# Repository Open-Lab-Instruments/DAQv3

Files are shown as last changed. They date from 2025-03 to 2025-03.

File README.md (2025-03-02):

# DAQv3
A Dual-Channel, Low Noise, Modular, 100 kHz Bandwidth, 24-Bit Data Acquisition (DAQ) Device / FFT Signal Analyzer

# Table of Contents

- **[Introduction](#introduction)**
- **[CAD Model](#cad-model)**
- **[Modules](#modules)**
  - [AnalogConversion_v1](#AnalogConversion_v1)
  - [AnalogConversion_v2](#AnalogConversion_v2)
  - [AnalogConversion_v3](#AnalogConversion_v3)
  - [Backplane_v1](#Backplane_v1)
  - [DigitalBackend_v1](#DigitalBackend_v1)
  - [PowerSupply_5V_v1](#PowerSupply_5V_v1)
  - [PowerSupply_5V_v2](#PowerSupply_5V_v2)
  - [PowerSupply_12V_v1](#PowerSupply_12V_v1)
  - [PowerSupply_12V_v2](#PowerSupply_12V_v2)
  - [USBConnectors_v1](#USBConnectors_v1)
- **[Firmware](#firmware)**
- **[USB Driver](#usb-driver)**
- **[Debug and Control Interface](#debug-and-control-interface)**
- **[Measurement Results](#measurement-results)**
  - [Linear Power Supply vs. Switched-Mode Power Supply](#linear-power-supply-vs-switched-mode-power-supply)
  - [Differential Input Module (AnalogConversion_v3)](#differential-input-module-analogconversion_v3)

# Introduction

Work in progress ...

# Rack
+ [Card Rail](https://it.rs-online.com/web/p/montanti-rack/2457848)
+ [Front Pannel Large](https://it.rs-online.com/web/p/accessori-per-contenitori/2879769) (10 HP)
+ [Front Pannel Small](https://us.rs-online.com/product/nvent-schroff/20848664/70294016/)  (4 HP)
+ [Case](https://it.rs-online.com/web/p/contenitori-e-scatole-rack/2550700?searchId=d65bfb2c-882b-444f-99ba-9c0d112e01d9&gb=s)  (42 HP)
+ [IEC Connector](https://it.rs-online.com/web/p/filtri-iec/8703669)

# CAD Model

The complete CAD model can be downloaded <a href="https://github.com/yildi1337/DAQv3/tree/main/cad_complete/inventor">here</a> (Autodesk Inventor 2023 files) including all <a href="#modules">modules</a> and the case.

<p align="center">
    
</p>

# Modules

## AnalogConversion_v1

- [Schematics (PDF)](https://github.com/yildi1337/DAQv3/blob/main/schematics/AnalogConversion_v1_Schematics.pdf)
- [Schematics (Eagle)](https://github.com/yildi1337/DAQv3/blob/main/eagle/AnalogConversion_v1.sch)
- [Board (Eagle)](https://github.com/yildi1337/DAQv3/blob/main/eagle/AnalogConversion_v1.brd)
- [Gerber Files](https://github.com/yildi1337/DAQv3/blob/main/pcb_gerber/AnalogConversion_v1_2022-03-20.zip)
- [3D Step File](https://github.com/yildi1337/DAQv3/blob/main/cad_modules_step/AnalogConversion_v1.step)
- [Bill of Materials](https://github.com/yildi1337/DAQv3/blob/main/pcb_bom/BOM_AnalogConversion_v1.txt)

<p align="center">
    
</p>

## AnalogConversion_v2

- [Schematics (PDF)](https://github.com/yildi1337/DAQv3/blob/main/schematics/AnalogConversion_v2_Schematics.pdf)
- [Schematics (Eagle)](https://github.com/yildi1337/DAQv3/blob/main/eagle/AnalogConversion_v2.sch)
- [Board (Eagle)](https://github.com/yildi1337/DAQv3/blob/main/eagle/AnalogConversion_v2.brd)
- [Gerber Files](https://github.com/yildi1337/DAQv3/blob/main/pcb_gerber/AnalogConversion_v2_2022-05-25.zip)
- [3D Step File](https://github.com/yildi1337/DAQv3/blob/main/cad_modules_step/AnalogConversion_v2.step)
- [Bill of Materials](https://github.com/yildi1337/DAQv3/blob/main/pcb_bom/BOM_AnalogConversion_v2.txt)

<p align="center">
    
</p>

## AnalogConversion_v3

- [Schematics (PDF)](https://github.com/yildi1337/DAQv3/blob/main/schematics/AnalogConversion_v3_Schematics.pdf)
- [Schematics (Eagle)](https://github.com/yildi1337/DAQv3/blob/main/eagle/AnalogConversion_v3.sch)
- [Board (Eagle)](https://github.com/yildi1337/DAQv3/blob/main/eagle/AnalogConversion_v3.brd)
- [Gerber Files](https://github.com/yildi1337/DAQv3/blob/main/pcb_gerber/AnalogConversion_v3_2022-07-25.zip)
- [3D Step File](https://github.com/yildi1337/DAQv3/blob/main/cad_modules_step/AnalogConversion_v3.step)
- [Bill of Materials](https://github.com/yildi1337/DAQv3/blob/main/pcb_bom/BOM_AnalogConversion_v3.txt)

<p align="center">
    
</p>

## Backplane_v1

- [Schematics (PDF)](https://github.com/yildi1337/DAQv3/blob/main/schematics/Backplane_v1_Schematics.pdf)
- [Schematics (Eagle)](https://github.com/yildi1337/DAQv3/blob/main/eagle/Backplane_v1.sch)
- [Board (Eagle)](https://github.com/yildi1337/DAQv3/blob/main/eagle/Backplane_v1.brd)
- [Gerber Files](https://github.com/yildi1337/DAQv3/blob/main/pcb_gerber/Backplane_v1_2022-03-20.zip)
- [3D Step File](https://github.com/yildi1337/DAQv3/blob/main/cad_modules_step/Backplane_v1.step)
- [Bill of Materials](https://github.com/yildi1337/DAQv3/blob/main/pcb_bom/BOM_Backplane_v1.txt)

<p align="center">
    
</p>

## DigitalBackend_v1

- [Schematics (PDF)](https://github.com/yildi1337/DAQv3/blob/main/schematics/DigitalBackend_v1_Schematics.pdf)
- [Schematics (Eagle)](https://github.com/yildi1337/DAQv3/blob/main/eagle/DigitalBackend_v1.sch)
- [Board (Eagle)](https://github.com/yildi1337/DAQv3/blob/main/eagle/DigitalBackend_v1.brd)
- [Gerber Files](https://github.com/yildi1337/DAQv3/blob/main/pcb_gerber/DigitalBackend_v1_2022-03-20.zip)
- [3D Step File](https://github.com/yildi1337/DAQv3/blob/main/cad_modules_step/DigitalBackend_v1.step)
- [Bill of Materials](https://github.com/yildi1337/DAQv3/blob/main/pcb_bom/BOM_DigitalBackend_v1.txt)

<p align="center">
    
</p>

## PowerSupply_12V_v1

- [Schematics (PDF)](https://github.com/yildi1337/DAQv3/blob/main/schematics/PowerSupply_12V_v1_Schematics.pdf)
- [Schematics (Eagle)](https://github.com/yildi1337/DAQv3/blob/main/eagle/PowerSupply_12V_v1.sch)
- [Board (Eagle)](https://github.com/yildi1337/DAQv3/blob/main/eagle/PowerSupply_12V_v1.brd)
- [Gerber Files](https://github.com/yildi1337/DAQv3/blob/main/pcb_gerber/PowerSupply_12V_v1_2022-03-20.zip)
- [3D Step File](https://github.com/yildi1337/DAQv3/blob/main/cad_modules_step/PowerSupply_12V_v1.step)
- [Bill of Materials](https://github.com/yildi1337/DAQv3/blob/main/pcb_bom/BOM_PowerSupply_12V_v1.txt)

<p align="center">
    
</p>

## PowerSupply_12V_v2

- [Schematics (PDF)](https://github.com/yildi1337/DAQv3/blob/main/schematics/PowerSupply_12V_v2_Schematics.pdf)
- [Schematics (Eagle)](https://github.com/yildi1337/DAQv3/blob/main/eagle/PowerSupply_12V_v2.sch)
- [Board (Eagle)](https://github.com/yildi1337/DAQv3/blob/main/eagle/PowerSupply_12V_v2.brd)
- [Gerber Files](https://github.com/yildi1337/DAQv3/blob/main/pcb_gerber/PowerSupply_12V_v2_2022-05-25.zip)
- [3D Step File](https://github.com/yildi1337/DAQv3/blob/main/cad_modules_step/PowerSupply_12V_v2.step)
- [Bill of Materials](https://github.com/yildi1337/DAQv3/blob/main/pcb_bom/BOM_PowerSupply_12V_v2.txt)

<p align="center">
    
</p>

## PowerSupply_5V_v1

- [Schematics (PDF)](https://github.com/yildi1337/DAQv3/blob/main/schematics/PowerSupply_5V_v1_Schematics.pdf)
- [Schematics (Eagle)](https://github.com/yildi1337/DAQv3/blob/main/eagle/PowerSupply_5V_v1.sch)
- [Board (Eagle)](https://github.com/yildi1337/DAQv3/blob/main/eagle/PowerSupply_5V_v1.brd)
- [Gerber Files](https://github.com/yildi1337/DAQv3/blob/main/pcb_gerber/PowerSupply_5V_v1_2022-03-20.zip)
- [3D Step File](https://github.com/yildi1337/DAQv3/blob/main/cad_modules_step/PowerSupply_5V_v1.step)
- [Bill of Materials](https://github.com/yildi1337/DAQv3/blob/main/pcb_bom/BOM_PowerSupply_5V_v1.txt)

<p align="center">
    
</p>

## PowerSupply_5V_v2

- [Schematics (PDF)](https://github.com/yildi1337/DAQv3/blob/main/schematics/PowerSupply_5V_v2_Schematics.pdf)
- [Schematics (Eagle)](https://github.com/yildi1337/DAQv3/blob/main/eagle/PowerSupply_5V_v2.sch)
- [Board (Eagle)](https://github.com/yildi1337/DAQv3/blob/main/eagle/PowerSupply_5V_v2.brd)
- [Gerber Files](https://github.com/yildi1337/DAQv3/blob/main/pcb_gerber/PowerSupply_5V_v2_2022-05-25.zip)
- [3D Step File](https://github.com/yildi1337/DAQv3/blob/main/cad_modules_step/PowerSupply_5V_v2.step)
- [Bill of Materials](https://github.com/yildi1337/DAQv3/blob/main/pcb_bom/BOM_PowerSupply_5V_v2.txt)

<p align="center">
    
</p>

## USBConnectors_v1

- [Schematics (PDF)](https://github.com/yildi1337/DAQv3/blob/main/schematics/USBConnectors_v1_Schematics.pdf)
- [Schematics (Eagle)](https://github.com/yildi1337/DAQv3/blob/main/eagle/USBConnectors_v1.sch)
- [Board (Eagle)](https://github.com/yildi1337/DAQv3/blob/main/eagle/USBConnectors_v1.brd)
- [Gerber Files](https://github.com/yildi1337/DAQv3/blob/main/pcb_gerber/USBConnectors_v1_2022-03-14.zip)
- [3D Step File](https://github.com/yildi1337/DAQv3/blob/main/cad_modules_step/USBConnectors_v1.step)
- [Bill of Materials](https://github.com/yildi1337/DAQv3/blob/main/pcb_bom/BOM_USBConnectors_v1.txt)

<p align="center">
    
</p>

# Firmware

The firmware running on the STM32H753ZIT6 is mainly written in ANSI C and has been developed in <a href="https://www.st.com/en/development-tools/stm32cubeide.html">STM32CubeIDE</a> version 1.10.1 utilizing the official <a href="https://github.com/STMicroelectronics/stm32h7xx_hal_driver">STM32H7xx_HAL_Driver</a>. Among others, the firmware performs the following tasks:

- Configuration of the ADC AD7768 (on module <a href="#AnalogConversion_v3">AnalogConversion_v3</a>) via SPI (SPI_3).
- Reception of sampled data from the ADC AD7768 via SPI (SPI_2) and DMA (DMA1_Stream0).
- Transmission of sampled data from the ADC AD7768 via USB 2.0 Hi-Speed to the PC utilizing ULPI interface and an additional Hi-Speed USB PHY (USB3300).
- Handling USART connection (USART_1, via FT232RL chip on <a href="#USBConnectors_v1">USBConnectors_v1</a>) for debug purposes and for exchanging control/status commands with the PC.
- Controlling I2C bus (I2C_4) for controlling I/O expander TCA9534A (e.g. on module <a href="#AnalogConversion_v3">AnalogConversion_v3</a>) which, in turn, drives a relay driver (MAX4820) on the same module.
- Controlling front LEDs (on module <a href="#DigitalBackend_v1">DigitalBackend_v1</a>).

The complete source code can be found <a href="https://github.com/yildi1337/DAQv3/tree/main/firmware">here</a>.

# USB Driver

Two USB drivers are needed for operating the DAQ v3:

- For the reception of the sampled data from the ADC NI-VISA is utilized. The driver matching the hardware of this project has been generated with the NI-VISA Driver Wizard an can be downloaded <a href="https://github.com/yildi1337/DAQv3/tree/main/usb_driver/ni-visa">here</a>.
- To use the USB debug interface only the official USB serial driver from FTDI is required, which can be downloaded <a href="https://github.com/yildi1337/DAQv3/tree/main/usb_driver/ftdi">here</a>.

# Debug and Control Interface

Tool for graphical display of status information and for controlling the hardware via the virtual serial interface (second USB-B port). The python source code and a binary (only tested on x64 Microsoft Windows 10) can be downloaded <a href="https://github.com/yildi1337/DAQv3/tree/main/debug_interface">here</a>. 

<p align="center">
    
</p>

# Measurement Results

## Linear Power Supply vs. Switched-Mode Power Supply

Noise measurements (60 seconds) were performed while powering the electronics with the power supplies of versions v1 and v2, where the abbreviations PS and ACNV in the titles refer to the power supply and analog conversion modules.

The two linear power supply modules of version v1 both operate with transformers. This resulted in heavy magnetic interference in the form of the mains frequency and multiples thereof.

The two power supply modules of version v2 both operate with AC/DC power modules (<a href="https://www.tracopower.com/de/deu/model/tmlm-20105">TMLM 20105</a>, <a href="https://www.tracopower.com/de/deu/model/tmlm-20115">TMLM 20115</a>) from Traco Power. Their switching frequencies are around 132 +/- 8 kHz and thus above the useful range of 0 - 100 kHz (Nyquist frequency is 128 kHz).

<p align="center">
    
</p>

## Differential Input Module (AnalogConversion_v3)

The investigated setup consists of the modules:

- <a href="#Backplane_v1">Backplane_v1</a>
- <a href="#PowerSupply_5V_v2">PowerSupply_5V_v2</a>
- <a href="#PowerSupply_12V_v2">PowerSupply_12V_v2</a>
- <a href="#AnalogConversion_v3">AnalogConversion_v3</a>
- <a href="#DigitalBackend_v1">DigitalBackend_v1</a>
- <a href="#USBConnectors_v1">USBConnectors_v1</a>

### Mains Interference and Grounding

The two differential inputs of each channel were connected via <a href="https://www.mouser.de/ProductDetail/Amphenol-RF/132360?qs=V8V9vCxO5JtDrelx3RqrVA%3D%3D">50 Ohm SMA resistors</a> with AGND (SHIELD connected via R6 = 0 Ohm with AGND, <a href="https://github.com/yildi1337/DAQv3/blob/main/schematics/AnalogConversion_v3_Schematics.pdf">see schematics</a>).

<p align="center">
    
</p>

Obviously, the lowest interference occurs in grounded mode and when GND of the backplane is directly connected to the chassis/the protective earth connector of the power entry module (first plot).

### Input Noise of Differential Opamp Driver and ADC

The measurement result from above is essential for the further development of the preamplifier. The gain of the preamplifier must be high enough to be able to neglect the noise from the opamp driver (ADA4945-1) and ADC (AD7768-4) determined here. A useful model for describing the power spectral density of the voltage noise $PSD(f)$ (in units of $\mathrm{V}^2/\mathrm{Hz}$) is the polynomial law 
$$\mathrm{PSD}(f) = \mathrm{LSD}^2(f) = \sum_{i=-1}^{0} b_i f^i$$ 
where $i=0$ and $i=-1$ refer to white noise and $1/f$ flicker noise, respectively, and $\mathrm{LSD}(f)$ referes to the linear spectrum density (in units of $\mathrm{V}/\sqrt{\mathrm{Hz}}$). For this measurement, values of
- $b_{-1} = 1.3 \cdot 10^{-13}~\mathrm{V}^2$
- $b_0 = {1.3 \cdot 10^{-15}~\mathrm{V}^2/\mathrm{Hz}}$
were found.

This results in a $1/f$ corner frequency of $f_{\mathrm{c}} = b_{-1}/b_0 = 100~\mathrm{Hz}$. The white voltage noise density is equal to $\sqrt{b_0} = 36~\mathrm{nV}/\sqrt{\mathrm{Hz}}$. Based on the two time domain noise signals RMS noise values of $13.2~\mu\mathrm{V}$ (channel 1) and $13.5~\mu\mathrm{V}$ (channel 2) were determined after substracting the DC offsets of $-6.5~\mathrm{mV}$ and $-1.8~\mathrm{mV}$.

The measured RMS noise values are in good agreement with the value of $11.58~\mu\mathrm{V}$ given in the datasheet (for the ADC only).

<p align="center">
    
</p>

In addition, for $V_{\mathrm{ref}} = 5~\mathrm{V}$, the dynamic range of the utilized combination of opamp driver and ADC is better than 

$$\mathrm{DR} = 20 \cdot \log_{10}\left(\frac{2 \cdot V_{\mathrm{ref}}}{\sqrt{2} \cdot \mathrm{RMS}\ \mathrm{noise}}\right)~\mathrm{dB} = 114\ \mathrm{dB}$$ 

### ADC RAW Data for Several Input Configurations

<p align="center">
    
</p>

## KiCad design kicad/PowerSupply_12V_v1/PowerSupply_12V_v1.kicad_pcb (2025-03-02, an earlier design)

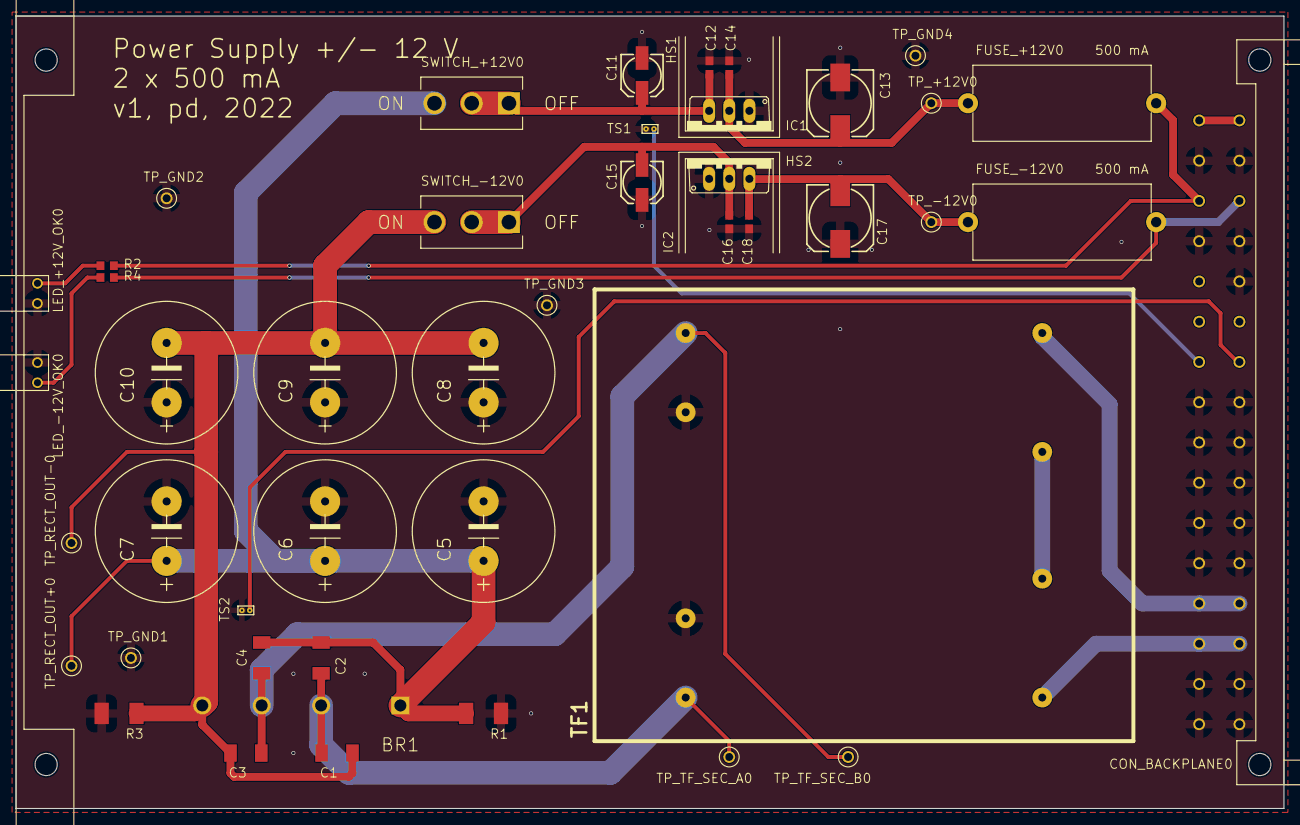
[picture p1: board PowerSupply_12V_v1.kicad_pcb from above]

Board: 2 copper layers, 160.0 x 100.0 mm, 48 parts (0 on the bottom side), 19 nets.

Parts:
BR1: GBJ610; GBJ610_24264370
C1, C2, C3, C4: 10n/1kV; C1808_18640681
C5, C6, C7, C8, C9, C10: 10000u/25V; EEUHD1E103_33731490
C11, C15: 22u/25V; 153CLV-0505_18640681
C12, C14, C16, C18: 100n; C0603_18640681
C13, C17: 100u/25V; 153CLV-0810_18640681
CON_BACKPLANE0: 09031326921; 09031326921_33573412
FUSE_+12V0: 0031.8201; 0031.8201_24323731
FUSE_-12V0: 0031.8201; 0031.8201_24323731
HS1, HS2: FK 237 SA 220 O; FK_237_SA_220_O_33584193
IC1: LM1085IT-12; LM1085IT-12_33765943
IC2: LM2990T-12; LM2990T-12_33765966
LED_+12V_OK0: 113-314-04; 113-314-04_33630242
LED_-12V_OK0: 113-314-04; 113-314-04_33630242
PCB_BRACKET0: 60807-011; 60807-011_33573280
R1, R3: 360/2W; R2010_18640681
R2, R4: 680; R0603_18640681
SWITCH_+12V0: RSPRO-SPDT-SLIDE-SWITCH-7347334; RSPRO-SPDT-SLIDE-SWITCH-7347334_23627966
SWITCH_-12V0: RSPRO-SPDT-SLIDE-SWITCH-7347334; RSPRO-SPDT-SLIDE-SWITCH-7347334_23627966
TF1: FL 24/12; FL_24-12_33729599
TP_+12V0: RSPRO-1MM-TERMINAL-POST-2622034_23908750
TP_-12V0: RSPRO-1MM-TERMINAL-POST-2622034_23908750
TP_GND1, TP_GND2, TP_GND3, TP_GND4: RSPRO-1MM-TERMINAL-POST-2622034_23908750
TP_RECT_OUT+0: RSPRO-1MM-TERMINAL-POST-2622034_23908750
TP_RECT_OUT-0: RSPRO-1MM-TERMINAL-POST-2622034_23908750
TP_TF_SEC_A0: RSPRO-1MM-TERMINAL-POST-2622034_23908750
TP_TF_SEC_B0: RSPRO-1MM-TERMINAL-POST-2622034_23908750
TS1, TS2: NB-PTCO-160; NB-PTCO-160_24346792

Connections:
+5V: CON_BACKPLANE0.1, CON_BACKPLANE0.2
+12V: CON_BACKPLANE0.5, FUSE_+12V0.2, R2.2
-12V: CON_BACKPLANE0.6, FUSE_-12V0.2, R4.1
BITE_PS_12V_TS1: CON_BACKPLANE0.13, TS1.1
BITE_PS_12V_TS2: CON_BACKPLANE0.14, TS2.1
GND: C5.-, C6.-, C7.-, C8.+, C9.+, C10.+, C11.-, C12.2, C13.-, C14.2, C15.+, C16.1, C17.+, C18.1, CON_BACKPLANE0.3, CON_BACKPLANE0.4, CON_BACKPLANE0.7, CON_BACKPLANE0.8, CON_BACKPLANE0.10, CON_BACKPLANE0.15, CON_BACKPLANE0.16, CON_BACKPLANE0.17, CON_BACKPLANE0.18, CON_BACKPLANE0.19, CON_BACKPLANE0.20, CON_BACKPLANE0.21, CON_BACKPLANE0.22, CON_BACKPLANE0.23, CON_BACKPLANE0.24, CON_BACKPLANE0.29, CON_BACKPLANE0.30, CON_BACKPLANE0.31, CON_BACKPLANE0.32, IC1.1, IC2.1, LED_+12V_OK0.-, LED_-12V_OK0.+, R1.1, R3.2, TF1.S1B, TF1.S2A, TP_GND1.P$1, TP_GND2.P$1, TP_GND3.P$1, TP_GND4.P$1, TS1.2, TS2.2
L: CON_BACKPLANE0.27, CON_BACKPLANE0.28, TF1.P1A
N: CON_BACKPLANE0.25, CON_BACKPLANE0.26, TF1.P2B
unnamed: C15.-, C16.2, IC2.2, SWITCH_-12V0.1, SWITCH_-12V0.2
unnamed: LED_-12V_OK0.-, R4.2
unnamed: C17.-, C18.2, FUSE_-12V0.1, IC2.3, TP_-12V0.P$1
unnamed: TF1.P1B, TF1.P2A
unnamed: BR1.L, C1.1, C2.1, TF1.S1A, TP_TF_SEC_A0.P$1
unnamed: LED_+12V_OK0.+, R2.1
unnamed: C13.+, C14.1, FUSE_+12V0.1, IC1.2, TP_+12V0.P$1
unnamed: BR1.N, C3.2, C4.2, TF1.S2B, TP_TF_SEC_B0.P$1
unnamed: C11.+, C12.1, IC1.3, SWITCH_+12V0.1, SWITCH_+12V0.2
RECT_OUT+: BR1.+, C2.2, C4.1, C5.+, C6.+, C7.+, R1.2, SWITCH_+12V0.3, TP_RECT_OUT+0.P$1
RECT_OUT-: BR1.-, C1.2, C3.1, C8.-, C9.-, C10.-, R3.1, SWITCH_-12V0.3, TP_RECT_OUT-0.P$1

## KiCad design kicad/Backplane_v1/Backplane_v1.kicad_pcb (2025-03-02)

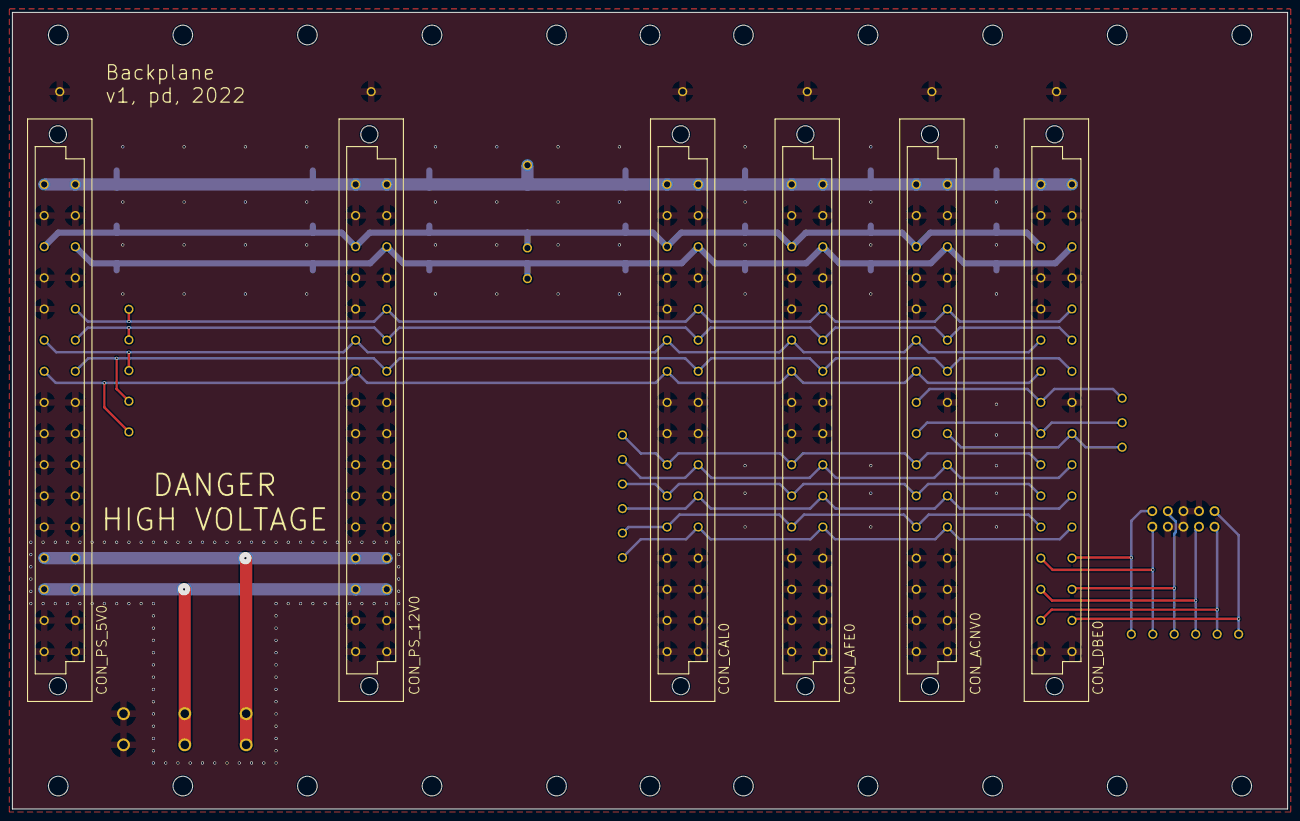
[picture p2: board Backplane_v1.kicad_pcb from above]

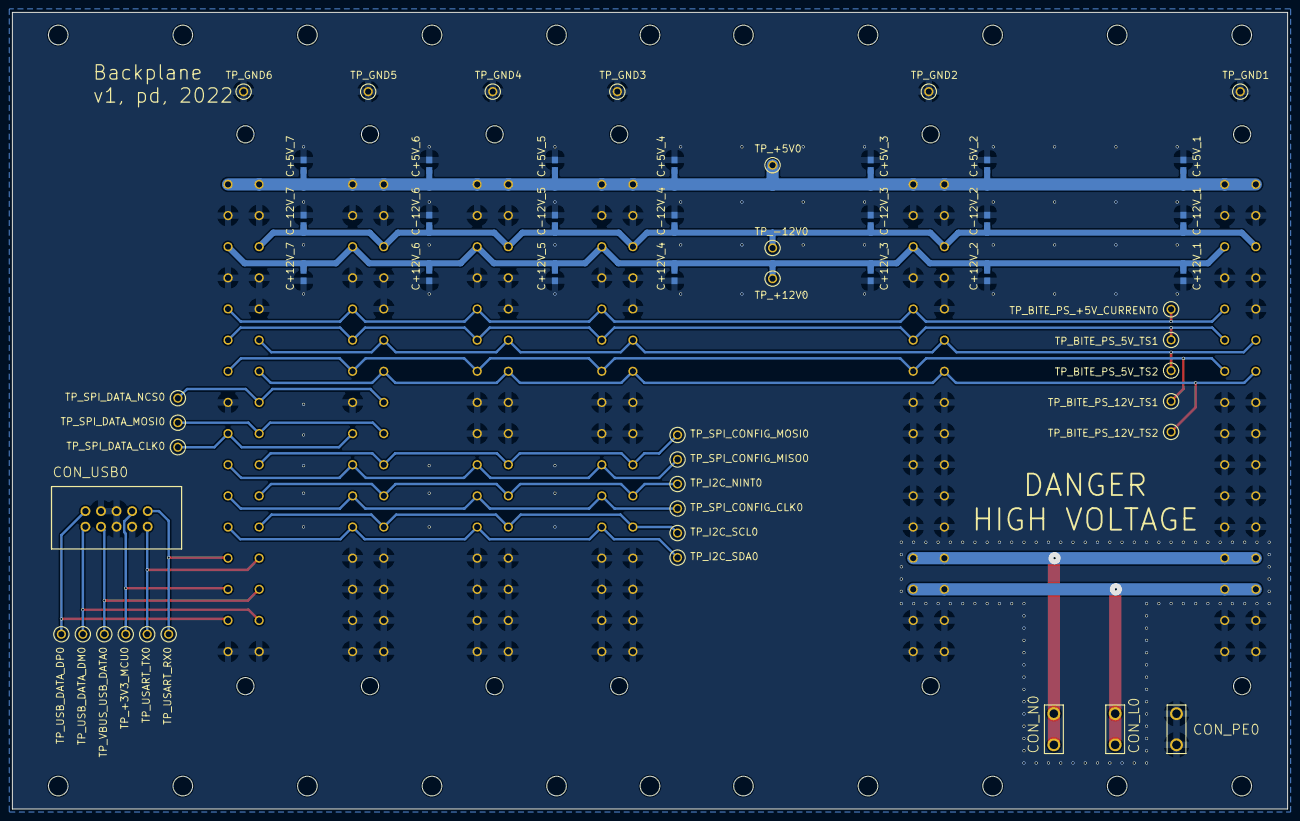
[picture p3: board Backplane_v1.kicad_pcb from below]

Board: 2 copper layers, 208.0 x 129.9 mm, 82 parts (54 on the bottom side), 26 nets.

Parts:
C+5V_1, C+5V_2, C+5V_3, C+5V_4, C+5V_5, C+5V_6, C+5V_7, C+12V_1, C+12V_2, C+12V_3, C+12V_4, C+12V_5, C+12V_6, C+12V_7: 100n; C0603_18640681
C-12V_1, C-12V_2, C-12V_3, C-12V_4, C-12V_5, C-12V_6, C-12V_7: 100n; C0603_18640681
CON_ACNV0: 09032326825; 09032326825_33780477
CON_AFE0: 09032326825; 09032326825_33780477
CON_CAL0: 09032326825; 09032326825_33780477
CON_DBE0: 09032326825; 09032326825_33780477
CON_L0: 63824-1; 63824-1_24300571
CON_N0: 63824-1; 63824-1_24300571
CON_PE0: 63824-1; 63824-1_24300571
CON_PS_5V0, CON_PS_12V0: 09032326825; 09032326825_33780477
CON_USB0: TST-105-01-T-D; TST-105-01-T-D_27603653
TP_+3V3_MCU0, TP_+5V0, TP_+12V0: RSPRO-1MM-TERMINAL-POST-2622034_23908750
TP_-12V0: RSPRO-1MM-TERMINAL-POST-2622034_23908750
TP_BITE_PS_5V_TS1, TP_BITE_PS_5V_TS2, TP_BITE_PS_12V_TS1, TP_BITE_PS_12V_TS2: RSPRO-1MM-TERMINAL-POST-2622034_23908750
TP_BITE_PS_+5V_CURRENT0: RSPRO-1MM-TERMINAL-POST-2622034_23908750
TP_GND1, TP_GND2, TP_GND3, TP_GND4, TP_GND5, TP_GND6: RSPRO-1MM-TERMINAL-POST-2622034_23908750
TP_I2C_NINT0, TP_I2C_SCL0, TP_I2C_SDA0: RSPRO-1MM-TERMINAL-POST-2622034_23908750
TP_SPI_CONFIG_CLK0: RSPRO-1MM-TERMINAL-POST-2622034_23908750
TP_SPI_CONFIG_MISO0: RSPRO-1MM-TERMINAL-POST-2622034_23908750
TP_SPI_CONFIG_MOSI0: RSPRO-1MM-TERMINAL-POST-2622034_23908750
TP_SPI_DATA_CLK0: RSPRO-1MM-TERMINAL-POST-2622034_23908750
TP_SPI_DATA_MOSI0: RSPRO-1MM-TERMINAL-POST-2622034_23908750
TP_SPI_DATA_NCS0: RSPRO-1MM-TERMINAL-POST-2622034_23908750
TP_USART_RX0: RSPRO-1MM-TERMINAL-POST-2622034_23908750
TP_USART_TX0: RSPRO-1MM-TERMINAL-POST-2622034_23908750
TP_USB_DATA_DM0: RSPRO-1MM-TERMINAL-POST-2622034_23908750
TP_USB_DATA_DP0: RSPRO-1MM-TERMINAL-POST-2622034_23908750
TP_VBUS_USB_DATA0: RSPRO-1MM-TERMINAL-POST-2622034_23908750
UNK_HOLE_0: dummyfp0
UNK_HOLE_1: dummyfp1
UNK_HOLE_2: dummyfp2
UNK_HOLE_3: dummyfp3
UNK_HOLE_4: dummyfp4
UNK_HOLE_5: dummyfp5
UNK_HOLE_6: dummyfp6
UNK_HOLE_7: dummyfp7
UNK_HOLE_8: dummyfp8
UNK_HOLE_9: dummyfp9
UNK_HOLE_10: dummyfp10
UNK_HOLE_11: dummyfp11
UNK_HOLE_12: dummyfp12
UNK_HOLE_13: dummyfp13
UNK_HOLE_14: dummyfp14
UNK_HOLE_15: dummyfp15
UNK_HOLE_16: dummyfp16
UNK_HOLE_17: dummyfp17
UNK_HOLE_18: dummyfp18
UNK_HOLE_19: dummyfp19
UNK_HOLE_20: dummyfp20
UNK_HOLE_21: dummyfp21

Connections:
+3V3_MCU: CON_DBE0.27, CON_USB0.8, TP_+3V3_MCU0.P$1
+5V: C+5V_1.1, C+5V_2.1, C+5V_3.1, C+5V_4.1, C+5V_5.1, C+5V_6.1, C+5V_7.1, CON_ACNV0.1, CON_ACNV0.2, CON_AFE0.1, CON_AFE0.2, CON_CAL0.1, CON_CAL0.2, CON_DBE0.1, CON_DBE0.2, CON_PS_5V0.1, CON_PS_5V0.2, CON_PS_12V0.1, CON_PS_12V0.2, TP_+5V0.P$1
+12V: C+12V_1.1, C+12V_2.1, C+12V_3.1, C+12V_4.1, C+12V_5.1, C+12V_6.1, C+12V_7.1, CON_ACNV0.5, CON_AFE0.5, CON_CAL0.5, CON_DBE0.5, CON_PS_5V0.5, CON_PS_12V0.5, TP_+12V0.P$1
-12V: C-12V_1.1, C-12V_2.1, C-12V_3.1, C-12V_4.1, C-12V_5.1, C-12V_6.1, C-12V_7.1, CON_ACNV0.6, CON_AFE0.6, CON_CAL0.6, CON_DBE0.6, CON_PS_5V0.6, CON_PS_12V0.6, TP_-12V0.P$1
BITE_PS_5V_TS1: CON_ACNV0.11, CON_AFE0.11, CON_CAL0.11, CON_DBE0.11, CON_PS_5V0.11, CON_PS_12V0.11, TP_BITE_PS_5V_TS1.P$1
BITE_PS_5V_TS2: CON_ACNV0.12, CON_AFE0.12, CON_CAL0.12, CON_DBE0.12, CON_PS_5V0.12, CON_PS_12V0.12, TP_BITE_PS_5V_TS2.P$1
BITE_PS_12V_TS1: CON_ACNV0.13, CON_AFE0.13, CON_CAL0.13, CON_DBE0.13, CON_PS_5V0.13, CON_PS_12V0.13, TP_BITE_PS_12V_TS1.P$1
BITE_PS_12V_TS2: CON_ACNV0.14, CON_AFE0.14, CON_CAL0.14, CON_DBE0.14, CON_PS_5V0.14, CON_PS_12V0.14, TP_BITE_PS_12V_TS2.P$1
BITE_PS_+5V_CURRENT: CON_ACNV0.9, CON_AFE0.9, CON_CAL0.9, CON_DBE0.9, CON_PS_5V0.9, CON_PS_12V0.9, TP_BITE_PS_+5V_CURRENT0.P$1
GND: C+5V_1.2, C+5V_2.2, C+5V_3.2, C+5V_4.2, C+5V_5.2, C+5V_6.2, C+5V_7.2, C+12V_1.2, C+12V_2.2, C+12V_3.2, C+12V_4.2, C+12V_5.2, C+12V_6.2, C+12V_7.2, C-12V_1.2, C-12V_2.2, C-12V_3.2, C-12V_4.2, C-12V_5.2, C-12V_6.2, C-12V_7.2, CON_ACNV0.3, CON_ACNV0.4, CON_ACNV0.7, CON_ACNV0.8, CON_ACNV0.10, CON_ACNV0.15, CON_ACNV0.25, CON_ACNV0.26, CON_ACNV0.27, CON_ACNV0.28, CON_ACNV0.29, CON_ACNV0.30, CON_ACNV0.31, CON_ACNV0.32, CON_AFE0.3, CON_AFE0.4, CON_AFE0.7, CON_AFE0.8, CON_AFE0.10, CON_AFE0.15, CON_AFE0.16, CON_AFE0.17, CON_AFE0.18, CON_AFE0.25, CON_AFE0.26, CON_AFE0.27, CON_AFE0.28, CON_AFE0.29, CON_AFE0.30, CON_AFE0.31, CON_AFE0.32, CON_CAL0.3, CON_CAL0.4, CON_CAL0.7, CON_CAL0.8, CON_CAL0.10, CON_CAL0.15, CON_CAL0.16, CON_CAL0.17, CON_CAL0.18, CON_CAL0.25, CON_CAL0.26, CON_CAL0.27, CON_CAL0.28, CON_CAL0.29, CON_CAL0.30, CON_CAL0.31, CON_CAL0.32, CON_DBE0.3, CON_DBE0.4, CON_DBE0.7, CON_DBE0.8, CON_DBE0.10, CON_DBE0.15, CON_DBE0.31, CON_DBE0.32, CON_PE0.1, CON_PE0.2, CON_PS_5V0.3, CON_PS_5V0.4, CON_PS_5V0.7, CON_PS_5V0.8, CON_PS_5V0.10, CON_PS_5V0.15, CON_PS_5V0.16, CON_PS_5V0.17, CON_PS_5V0.18, CON_PS_5V0.19, CON_PS_5V0.20, CON_PS_5V0.21, CON_PS_5V0.22, CON_PS_5V0.23, CON_PS_5V0.24, CON_PS_5V0.29, CON_PS_5V0.30, CON_PS_5V0.31, CON_PS_5V0.32, CON_PS_12V0.3, CON_PS_12V0.4, CON_PS_12V0.7, CON_PS_12V0.8, CON_PS_12V0.10, CON_PS_12V0.15, CON_PS_12V0.16, CON_PS_12V0.17, CON_PS_12V0.18, CON_PS_12V0.19, CON_PS_12V0.20, CON_PS_12V0.21, CON_PS_12V0.22, CON_PS_12V0.23, CON_PS_12V0.24, CON_PS_12V0.29, CON_PS_12V0.30, CON_PS_12V0.31, CON_PS_12V0.32, CON_USB0.4, CON_USB0.5, CON_USB0.6, CON_USB0.7, TP_GND1.P$1, TP_GND2.P$1, TP_GND3.P$1, TP_GND4.P$1, TP_GND5.P$1, TP_GND6.P$1
I2C_NINT: CON_ACNV0.22, CON_AFE0.22, CON_CAL0.22, CON_DBE0.22, TP_I2C_NINT0.P$1
I2C_SCL: CON_ACNV0.24, CON_AFE0.24, CON_CAL0.24, CON_DBE0.24, TP_I2C_SCL0.P$1
I2C_SDA: CON_ACNV0.23, CON_AFE0.23, CON_CAL0.23, CON_DBE0.23, TP_I2C_SDA0.P$1
L: CON_L0.1, CON_L0.2, CON_PS_5V0.27, CON_PS_5V0.28, CON_PS_12V0.27, CON_PS_12V0.28
N: CON_N0.1, CON_N0.2, CON_PS_5V0.25, CON_PS_5V0.26, CON_PS_12V0.25, CON_PS_12V0.26
SPI_CONFIG_CLK: CON_ACNV0.21, CON_AFE0.21, CON_CAL0.21, CON_DBE0.21, TP_SPI_CONFIG_CLK0.P$1
SPI_CONFIG_MISO: CON_ACNV0.19, CON_AFE0.19, CON_CAL0.19, CON_DBE0.19, TP_SPI_CONFIG_MISO0.P$1
SPI_CONFIG_MOSI: CON_ACNV0.20, CON_AFE0.20, CON_CAL0.20, CON_DBE0.20, TP_SPI_CONFIG_MOSI0.P$1
SPI_DATA_CLK: CON_ACNV0.17, CON_DBE0.17, TP_SPI_DATA_CLK0.P$1
SPI_DATA_MOSI: CON_ACNV0.18, CON_DBE0.18, TP_SPI_DATA_MOSI0.P$1
SPI_DATA_NCS: CON_ACNV0.16, CON_DBE0.16, TP_SPI_DATA_NCS0.P$1
USART_RX: CON_DBE0.25, CON_USB0.10, TP_USART_RX0.P$1
USART_TX: CON_DBE0.26, CON_USB0.9, TP_USART_TX0.P$1
USB_DATA_DM: CON_DBE0.30, CON_USB0.1, TP_USB_DATA_DM0.P$1
USB_DATA_DP: CON_DBE0.29, CON_USB0.2, TP_USB_DATA_DP0.P$1
VBUS_USB_DATA: CON_DBE0.28, CON_USB0.3, TP_VBUS_USB_DATA0.P$1

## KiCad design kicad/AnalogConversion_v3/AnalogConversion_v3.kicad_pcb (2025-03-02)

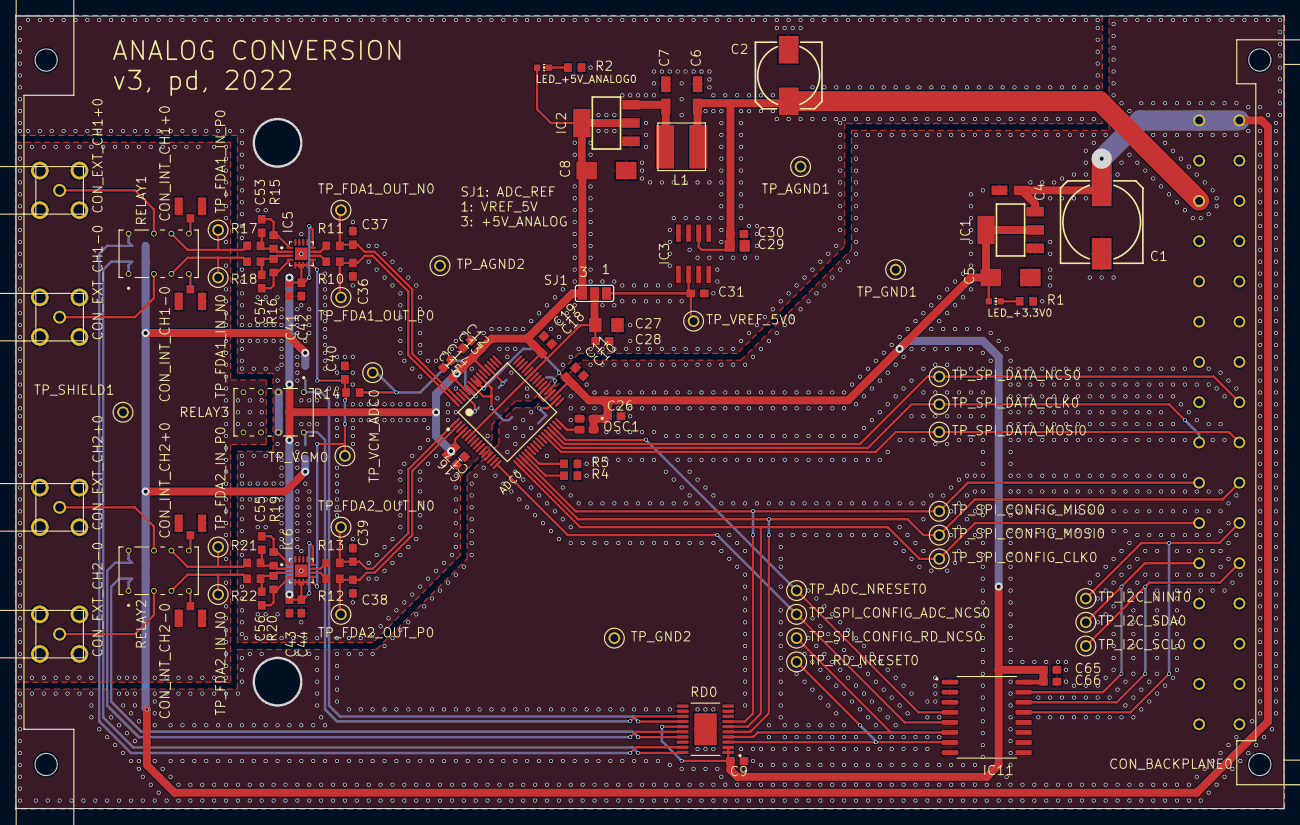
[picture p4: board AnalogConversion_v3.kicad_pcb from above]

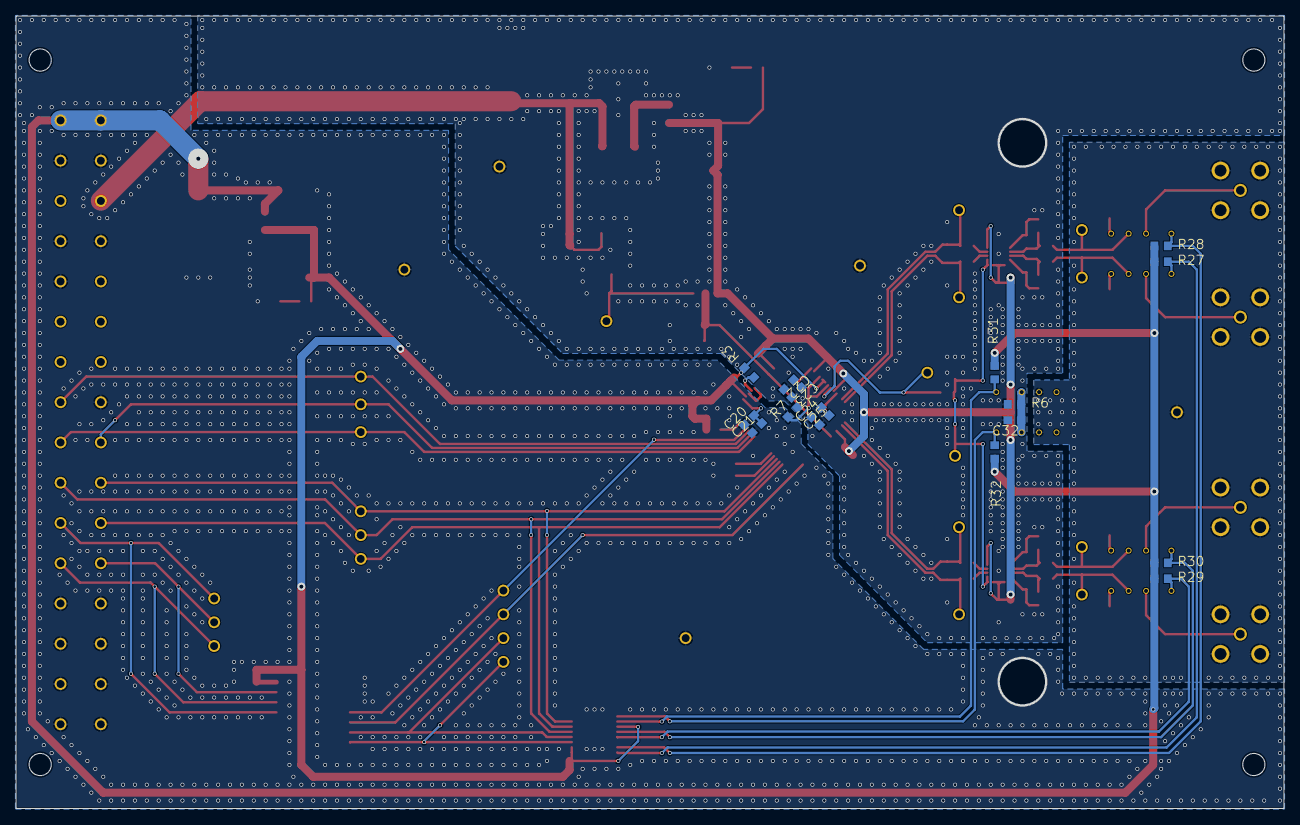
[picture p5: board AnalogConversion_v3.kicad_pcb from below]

Board: 2 copper layers, 160.0 x 100.0 mm, 127 parts (16 on the bottom side), 70 nets.

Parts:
ADC0: AD7768-4BSTZ; AD7768-4BSTZ_23633307
C1: 1000u/16V; 153CLV-1010_18640681
C2: 100u/25V; 153CLV-0810_18640681
C4, C6, C7: 10u; CT3216_23469469
C5, C8: 22u; CT6032_23469469
C9, C10, C12, C14, C16, C18, C20, C22, C24, C26, C28, C30, C31, C40, C42, C44, C66: 100n; C0603_23469469
C11, C13, C15, C17, C19, C23, C25, C41, C43, C65: 1u; C0603_23469469
C21: 10u; C0603_23469469
C27: 22u; C1206_23469469
C29: 10u/16V; C0805_23469469
C32: 10n; C0603_23469469
C36, C37, C38, C39: 82p; C0603_23469469
C53, C54, C55, C56: 220p; C0603_23469469
CON_BACKPLANE0: 09031326921; 09031326921_33573412
CON_EXT_CH1+0, CON_EXT_CH1-0, CON_EXT_CH2+0, CON_EXT_CH2-0: DELOCK_65848; DELOCK_65848_34726205
CON_INT_CH1+0, CON_INT_CH1-0, CON_INT_CH2+0, CON_INT_CH2-0: 2337019-1; 2337019-1_28281051
IC1: LM1117IMP-3.3; SOT223_23469477
IC2: LM1117MP-5.0; SOT223_23469477
IC3: ADR445ARZ; ADR445ARZ_35478497
IC5, IC6: ADA4945-1ACPZ-R7; ADA4945-1ACPZ-R7_22669072
IC11: TCA9534ADWR; TCA9534ADWR_34728514
L1: 100u; VLS6045AF-101M_31421361
LED_+3.3V0, LED_+5V_ANALOG0: CHIP-LED0603_259
OSC1: SG-210STF 32.7680ML3; SG-210STF-32.7680ML3_23634516
PCB_BRACKET0: 60807-011; 60807-011_33573280
R1: 750; R0603_23469469
R2: 1.8k; R0603_23469469
R3: 10k; R0603_23469469
R4, R5: 1k; R0603_23469469
R6: 1M; R0603_23469469
R7: 0; R0603_23469469
R10, R11, R12, R13: 82; R0603_23469469
R14: 47; R0603_23469469
R15, R16, R17, R18, R19, R20, R21, R22: 470; R0603_23469469
R27, R28, R29, R30, R31, R32: 100; R0603_23469469
RD0: MAX4820EUP+; MAX4820EUP+_31436371
RELAY1, RELAY2, RELAY3: 5-1462037-8; 5-1462037-8_31429267
SJ1: SJ_2_23508320
TP_ADC_NRESET0: RSPRO-1MM-TERMINAL-POST-2622034_23908750
TP_AGND1, TP_AGND2: RSPRO-1MM-TERMINAL-POST-2622034_23908750
TP_FDA1_IN_N0, TP_FDA1_IN_P0, TP_FDA1_OUT_N0, TP_FDA1_OUT_P0, TP_FDA2_IN_N0, TP_FDA2_IN_P0, TP_FDA2_OUT_N0, TP_FDA2_OUT_P0: RSPRO-1MM-TERMINAL-POST-2622034_23908750
TP_GND1, TP_GND2: RSPRO-1MM-TERMINAL-POST-2622034_23908750
TP_I2C_NINT0, TP_I2C_SCL0, TP_I2C_SDA0: RSPRO-1MM-TERMINAL-POST-2622034_23908750
TP_RD_NRESET0: RSPRO-1MM-TERMINAL-POST-2622034_23908750
TP_SHIELD1: RSPRO-1MM-TERMINAL-POST-2622034_23908750
TP_SPI_CONFIG_ADC_NCS0: RSPRO-1MM-TERMINAL-POST-2622034_23908750
TP_SPI_CONFIG_CLK0: RSPRO-1MM-TERMINAL-POST-2622034_23908750
TP_SPI_CONFIG_MISO0: RSPRO-1MM-TERMINAL-POST-2622034_23908750
TP_SPI_CONFIG_MOSI0: RSPRO-1MM-TERMINAL-POST-2622034_23908750
TP_SPI_CONFIG_RD_NCS0: RSPRO-1MM-TERMINAL-POST-2622034_23908750
TP_SPI_DATA_CLK0: RSPRO-1MM-TERMINAL-POST-2622034_23908750
TP_SPI_DATA_MOSI0: RSPRO-1MM-TERMINAL-POST-2622034_23908750
TP_SPI_DATA_NCS0: RSPRO-1MM-TERMINAL-POST-2622034_23908750
TP_VCM0: RSPRO-1MM-TERMINAL-POST-2622034_23908750
TP_VCM_ADC0: RSPRO-1MM-TERMINAL-POST-2622034_23908750
TP_VREF_5V0: RSPRO-1MM-TERMINAL-POST-2622034_23908750

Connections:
+3V3: ADC0.35, ADC0.56, ADC0.57, C5.+, C9.1, C10.1, C11.1, C26.2, C65.1, C66.1, IC1.2, IC1.TAB, IC11.16, LED_+3.3V0.A, OSC1.1, OSC1.4, R3.1, RD0.1, RD0.2, RD0.15
+5V: C1.+, C4.+, CON_BACKPLANE0.1, CON_BACKPLANE0.2, IC1.3, R27.2, R28.2, R29.2, R30.2, R31.2, R32.2
+5V_ANALOG: ADC0.4, ADC0.45, ADC0.53, ADC0.60, C8.+, C12.1, C13.1, C14.1, C15.1, C16.1, C17.1, C18.1, C19.1, C41.2, C42.2, C43.2, C44.2, IC2.2, IC2.TAB, IC5.5, IC5.6, IC5.7, IC5.8, IC5.12, IC6.5, IC6.6, IC6.7, IC6.8, IC6.12, LED_+5V_ANALOG0.A, SJ1.3
+12V: C2.+, C6.+, C29.2, C30.2, CON_BACKPLANE0.5, IC3.2, L1.1
ADC_AIN0_N: ADC0.63, C37.2, R11.1, TP_FDA1_OUT_N0.P$1
ADC_AIN0_P: ADC0.64, C36.1, R10.1, TP_FDA1_OUT_P0.P$1
ADC_AIN1_N: ADC0.1, C39.2, R13.1, TP_FDA2_OUT_N0.P$1
ADC_AIN1_P: ADC0.2, C38.1, R12.1, TP_FDA2_OUT_P0.P$1
ADC_MCLK: ADC0.32, OSC1.3
ADC_NRESET: ADC0.30, IC11.4, TP_ADC_NRESET0.P$1
ADC_REF: ADC0.6, ADC0.43, C27.1, C28.1, SJ1.2
AGND: ADC0.3, ADC0.5, ADC0.7, ADC0.8, ADC0.9, ADC0.10, ADC0.39, ADC0.40, ADC0.41, ADC0.42, ADC0.44, ADC0.46, ADC0.47, ADC0.48, ADC0.49, ADC0.50, ADC0.51, ADC0.54, ADC0.62, C2.-, C6.-, C7.-, C8.-, C12.2, C13.2, C14.2, C15.2, C16.2, C17.2, C18.2, C19.2, C22.2, C23.2, C24.2, C25.2, C27.2, C28.2, C29.1, C30.1, C31.1, C32.2, C36.2, C37.1, C38.2, C39.1, C40.2, C41.1, C42.1, C43.1, C44.1, IC2.1, IC3.4, IC5.13, IC5.14, IC5.15, IC5.16, IC5.17, IC6.13, IC6.14, IC6.15, IC6.16, IC6.17, R2.2, R6.2, R7.1, TP_AGND1.P$1, TP_AGND2.P$1
CON_EXT_CH1+: CON_EXT_CH1+0.S, RELAY1.7
CON_EXT_CH1-: CON_EXT_CH1-0.S, RELAY1.2
CON_EXT_CH2+: CON_EXT_CH2+0.S, RELAY2.7
CON_EXT_CH2-: CON_EXT_CH2-0.S, RELAY2.2
CON_INT_CH1+: CON_INT_CH1+0.S, RELAY1.5
CON_INT_CH1-: CON_INT_CH1-0.S, RELAY1.4
CON_INT_CH2+: CON_INT_CH2+0.S, RELAY2.5
CON_INT_CH2-: CON_INT_CH2-0.S, RELAY2.4
DIN: ADC0.21, R5.2
DNC/DGND: ADC0.20, R4.2
DREGCAP: ADC0.34, C20.1, C21.1
FDA1_IN_N: R18.2, RELAY1.3, TP_FDA1_IN_N0.P$1
FDA1_IN_P: R17.2, RELAY1.6, TP_FDA1_IN_P0.P$1
FDA2_IN_N: R22.2, RELAY2.3, TP_FDA2_IN_N0.P$1
FDA2_IN_P: R21.2, RELAY2.6, TP_FDA2_IN_P0.P$1
GND: ADC0.31, ADC0.33, ADC0.55, ADC0.58, C1.-, C4.-, C5.-, C9.2, C10.2, C11.2, C20.2, C21.2, C26.1, C65.2, C66.2, CON_BACKPLANE0.3, CON_BACKPLANE0.4, CON_BACKPLANE0.7, CON_BACKPLANE0.8, CON_BACKPLANE0.10, CON_BACKPLANE0.15, CON_BACKPLANE0.25, CON_BACKPLANE0.26, CON_BACKPLANE0.27, CON_BACKPLANE0.28, CON_BACKPLANE0.29, CON_BACKPLANE0.30, CON_BACKPLANE0.31, CON_BACKPLANE0.32, IC1.1, IC11.1, IC11.2, IC11.3, IC11.8, OSC1.2, R1.2, R4.1, R5.1, R7.2, RD0.9, RD0.12, RD0.18, RD0.21, TP_GND1.P$1, TP_GND2.P$1
I2C_NINT: CON_BACKPLANE0.22, IC11.13, TP_I2C_NINT0.P$1
I2C_SCL: CON_BACKPLANE0.24, IC11.14, TP_I2C_SCL0.P$1
I2C_SDA: CON_BACKPLANE0.23, IC11.15, TP_I2C_SDA0.P$1
unnamed: C32.1, R6.1, RELAY3.2, RELAY3.7
unnamed: C7.+, IC2.3, L1.2
unnamed: IC6.10, R12.2
unnamed: IC5.10, R10.2
unnamed: IC5.11, R11.2
unnamed: IC6.11, R13.2
unnamed: C53.1, IC5.2, R15.2, R17.1
unnamed: C53.2, IC5.1, R15.1
unnamed: C54.1, IC5.4, R16.1
unnamed: C54.2, IC5.3, R16.2, R18.1
unnamed: C55.1, IC6.2, R19.2, R21.1
unnamed: C55.2, IC6.1, R19.1
unnamed: C56.2, IC6.3, R20.2, R22.1
unnamed: C56.1, IC6.4, R20.1
unnamed: LED_+3.3V0.C, R1.1
unnamed: LED_+5V_ANALOG0.C, R2.1
unnamed: ADC0.36, ADC0.38
unnamed: ADC0.37, R3.2
RD_NRESET: IC11.7, RD0.3, TP_RD_NRESET0.P$1
RD_OUT1: R27.1, RD0.20, RELAY1.1
RD_OUT2: R28.1, RD0.19, RELAY1.8
RD_OUT3: R29.1, RD0.17, RELAY2.1
RD_OUT4: R30.1, RD0.16, RELAY2.8
RD_OUT5: R31.1, RD0.14, RELAY3.1
RD_OUT6: R32.1, RD0.13, RELAY3.8
REGCAPA: ADC0.61, C24.1, C25.1
REGCAPB: ADC0.52, C22.1, C23.1
SHIELD: CON_EXT_CH1+0.G1, CON_EXT_CH1+0.G2, CON_EXT_CH1+0.G3, CON_EXT_CH1+0.G4, CON_EXT_CH1-0.G1, CON_EXT_CH1-0.G2, CON_EXT_CH1-0.G3, CON_EXT_CH1-0.G4, CON_EXT_CH2+0.G1, CON_EXT_CH2+0.G2, CON_EXT_CH2+0.G3, CON_EXT_CH2+0.G4, CON_EXT_CH2-0.G1, CON_EXT_CH2-0.G2, CON_EXT_CH2-0.G3, CON_EXT_CH2-0.G4, CON_INT_CH1+0.G1, CON_INT_CH1+0.G2, CON_INT_CH1-0.G1, CON_INT_CH1-0.G2, CON_INT_CH2+0.G1, CON_INT_CH2+0.G2, CON_INT_CH2-0.G1, CON_INT_CH2-0.G2, RELAY3.3, RELAY3.6, TP_SHIELD1.P$1
SPI_CONFIG_ADC_NCS: ADC0.16, IC11.5, TP_SPI_CONFIG_ADC_NCS0.P$1
SPI_CONFIG_CLK: ADC0.17, CON_BACKPLANE0.21, RD0.6, TP_SPI_CONFIG_CLK0.P$1
SPI_CONFIG_MISO: ADC0.19, CON_BACKPLANE0.19, RD0.7, TP_SPI_CONFIG_MISO0.P$1
SPI_CONFIG_MOSI: ADC0.18, CON_BACKPLANE0.20, RD0.5, TP_SPI_CONFIG_MOSI0.P$1
SPI_CONFIG_RD_NCS: IC11.6, RD0.4, TP_SPI_CONFIG_RD_NCS0.P$1
SPI_DATA_CLK: ADC0.28, CON_BACKPLANE0.17, TP_SPI_DATA_CLK0.P$1
SPI_DATA_MOSI: ADC0.27, CON_BACKPLANE0.18, TP_SPI_DATA_MOSI0.P$1
SPI_DATA_NCS: ADC0.29, CON_BACKPLANE0.16, TP_SPI_DATA_NCS0.P$1
VCM: C40.1, IC5.9, IC6.9, R14.2, TP_VCM0.P$1
VCM_ADC: ADC0.59, R14.1, TP_VCM_ADC0.P$1
VREF_5V: C31.2, IC3.6, SJ1.1, TP_VREF_5V0.P$1

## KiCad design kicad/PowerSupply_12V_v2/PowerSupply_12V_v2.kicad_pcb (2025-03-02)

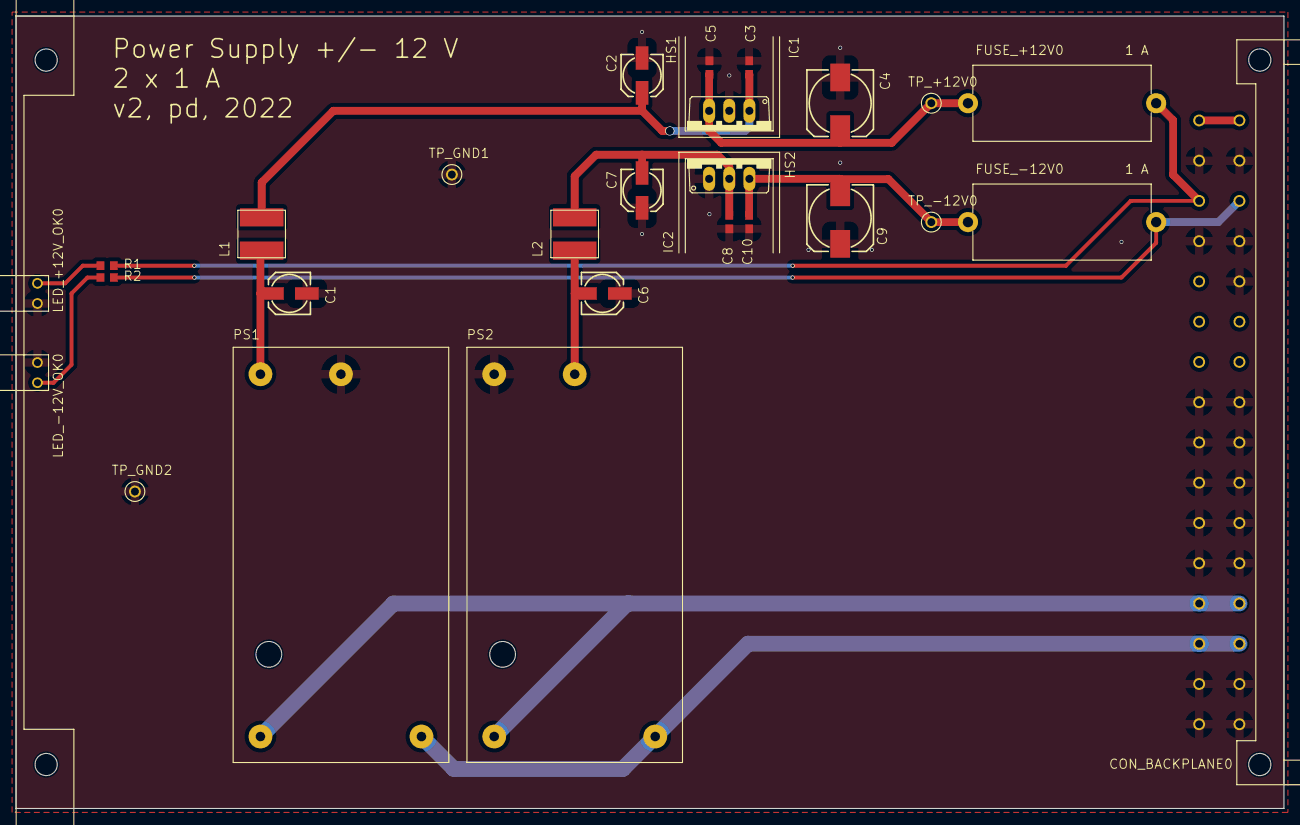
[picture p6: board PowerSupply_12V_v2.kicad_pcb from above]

Board: 2 copper layers, 160.0 x 100.0 mm, 30 parts (0 on the bottom side), 14 nets.

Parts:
C1, C2, C6, C7: 22u/25V; 153CLV-0505_18640681
C3, C5, C8, C10: 100n; C0603_18640681
C4, C9: 100u/25V; 153CLV-0810_18640681
CON_BACKPLANE0: 09031326921; 09031326921_33573412
FUSE_+12V0: 0031.8201; 0031.8201_24323731
FUSE_-12V0: 0031.8201; 0031.8201_24323731
HS1, HS2: FK 237 SA 220 O; FK_237_SA_220_O_33584193
IC1: L7812CV; L7812CV_35690097
IC2: L7912CV; L7912CV_35690127
L1, L2: VLS6045AF-101M; VLS6045AF-101M_31421361
LED_+12V_OK0: 113-314-04; 113-314-04_33630242
LED_-12V_OK0: 113-314-04; 113-314-04_33630242
PCB_BRACKET0: 60807-011; 60807-011_33573280
PS1, PS2: TMLM_20115; TMLM_201XX_35462927
R1, R2: 680; R0603_18640681
TP_+12V0: RSPRO-1MM-TERMINAL-POST-2622034_23908750
TP_-12V0: RSPRO-1MM-TERMINAL-POST-2622034_23908750
TP_GND1, TP_GND2: RSPRO-1MM-TERMINAL-POST-2622034_23908750

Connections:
+5V: CON_BACKPLANE0.1, CON_BACKPLANE0.2
+12V: CON_BACKPLANE0.5, FUSE_+12V0.2, R1.2
-12V: CON_BACKPLANE0.6, FUSE_-12V0.2, R2.1
GND: C1.-, C2.-, C3.2, C4.-, C5.2, C6.+, C7.+, C8.1, C9.+, C10.1, CON_BACKPLANE0.3, CON_BACKPLANE0.4, CON_BACKPLANE0.7, CON_BACKPLANE0.8, CON_BACKPLANE0.10, CON_BACKPLANE0.15, CON_BACKPLANE0.16, CON_BACKPLANE0.17, CON_BACKPLANE0.18, CON_BACKPLANE0.19, CON_BACKPLANE0.20, CON_BACKPLANE0.21, CON_BACKPLANE0.22, CON_BACKPLANE0.23, CON_BACKPLANE0.24, CON_BACKPLANE0.29, CON_BACKPLANE0.30, CON_BACKPLANE0.31, CON_BACKPLANE0.32, IC1.2, IC2.1, LED_+12V_OK0.-, LED_-12V_OK0.+, PS1.3, PS2.2, TP_GND1.P$1, TP_GND2.P$1
L: CON_BACKPLANE0.27, CON_BACKPLANE0.28, PS1.5, PS2.5
N: CON_BACKPLANE0.25, CON_BACKPLANE0.26, PS1.6, PS2.6
unnamed: C7.-, C8.2, IC2.2, L2.1
unnamed: LED_-12V_OK0.-, R2.2
unnamed: C9.-, C10.2, FUSE_-12V0.1, IC2.3, TP_-12V0.P$1
unnamed: C1.+, L1.1, PS1.2
unnamed: C6.-, L2.2, PS2.3
unnamed: LED_+12V_OK0.+, R1.1
unnamed: C4.+, C5.1, FUSE_+12V0.1, IC1.3, TP_+12V0.P$1
unnamed: C2.+, C3.1, IC1.1, L1.2

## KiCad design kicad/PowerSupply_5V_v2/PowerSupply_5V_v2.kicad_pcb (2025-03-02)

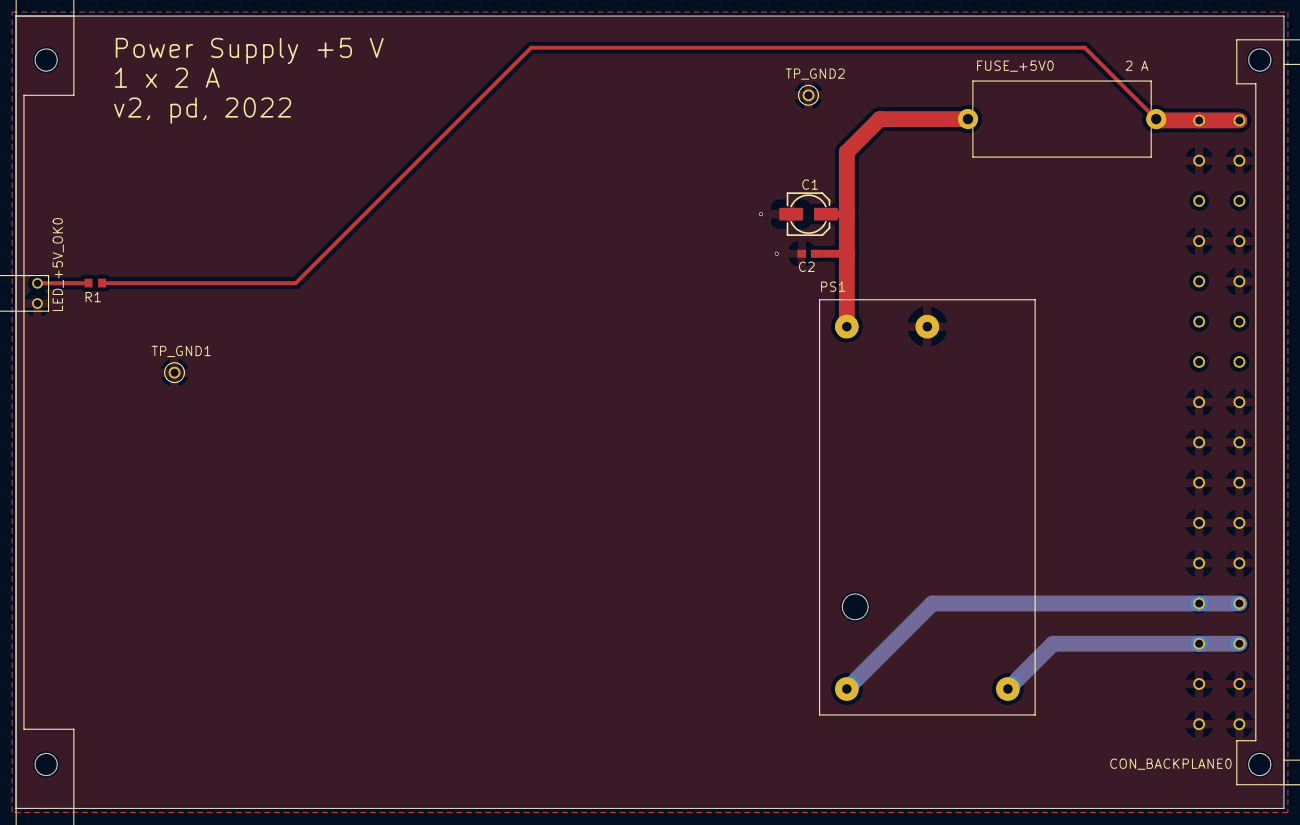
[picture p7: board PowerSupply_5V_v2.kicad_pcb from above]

Board: 2 copper layers, 160.0 x 100.0 mm, 10 parts (0 on the bottom side), 6 nets.

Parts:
C1: 47u/16V; 153CLV-0505_18640681
C2: 100n; C0603_18640681
CON_BACKPLANE0: 09031326921; 09031326921_33573412
FUSE_+5V0: 0031.8201; 0031.8201_24323731
LED_+5V_OK0: 113-314-04; 113-314-04_33630242
PCB_BRACKET0: 60807-011; 60807-011_33573280
PS1: TMLM_20105; TMLM_201XX_35462927
R1: 150; R0603_18640681
TP_GND1, TP_GND2: RSPRO-1MM-TERMINAL-POST-2622034_23908750

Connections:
+5V: CON_BACKPLANE0.1, CON_BACKPLANE0.2, FUSE_+5V0.2, R1.2
GND: C1.-, C2.2, CON_BACKPLANE0.3, CON_BACKPLANE0.4, CON_BACKPLANE0.7, CON_BACKPLANE0.8, CON_BACKPLANE0.10, CON_BACKPLANE0.15, CON_BACKPLANE0.16, CON_BACKPLANE0.17, CON_BACKPLANE0.18, CON_BACKPLANE0.19, CON_BACKPLANE0.20, CON_BACKPLANE0.21, CON_BACKPLANE0.22, CON_BACKPLANE0.23, CON_BACKPLANE0.24, CON_BACKPLANE0.29, CON_BACKPLANE0.30, CON_BACKPLANE0.31, CON_BACKPLANE0.32, LED_+5V_OK0.-, PS1.3, TP_GND1.P$1, TP_GND2.P$1
L: CON_BACKPLANE0.27, CON_BACKPLANE0.28, PS1.5
N: CON_BACKPLANE0.25, CON_BACKPLANE0.26, PS1.6
unnamed: C1.+, C2.1, FUSE_+5V0.1, PS1.2
unnamed: LED_+5V_OK0.+, R1.1

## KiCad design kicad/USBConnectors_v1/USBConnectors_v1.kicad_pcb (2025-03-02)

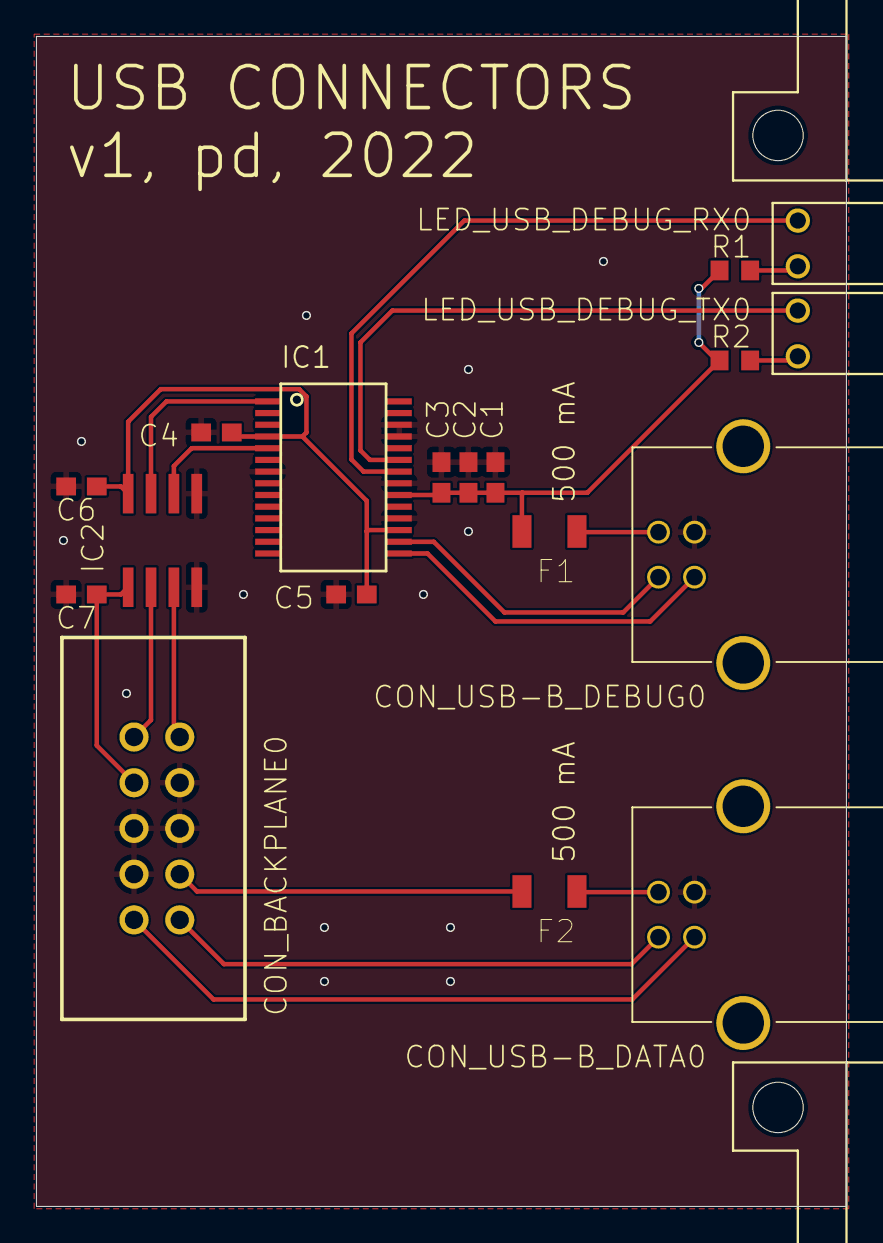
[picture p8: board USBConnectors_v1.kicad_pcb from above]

Board: 2 copper layers, 45.0 x 65.0 mm, 20 parts (0 on the bottom side), 19 nets.

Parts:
C1: 10n; C0603_23469469
C2, C4, C5, C6, C7: 100n; C0603_23469469
C3: 4.7u; C0603_23469469
CON_BACKPLANE0: TST-105-01-T-D; TST-105-01-T-D_27603653
CON_USB-B_DATA0: 61729-1011BLF; 61729-1011BLF_23524969
CON_USB-B_DEBUG0: 61729-1011BLF; 61729-1011BLF_23524969
F1, F2: 500 mA; LITTELFUSE_466_SERIES_24171630
IC1: FT232RL; FT232RL_24048598
IC2: ADUM1201ARZ; SO8_18370689
LED_USB_DEBUG_RX0: 113-311-04; 113-311-04_33651165
LED_USB_DEBUG_TX0: 113-305-04; 113-305-04_33651180
PCB_BRACKET1: 60807-181_A; 60807-181_A_33908866
PCB_BRACKET2: 60807-181_B; 60807-181_B_33908866
R1, R2: 1.5k; R0603_23469469

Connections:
GND: C1.2, C2.1, C3.1, C4.2, C5.2, C6.2, C7.1, CON_BACKPLANE0.4, CON_BACKPLANE0.5, CON_BACKPLANE0.6, CON_BACKPLANE0.7, CON_USB-B_DATA0.4, CON_USB-B_DEBUG0.4, IC1.7, IC1.18, IC1.21, IC1.25, IC1.26, IC2.4, IC2.5
unnamed: CON_USB-B_DEBUG0.1, F1.1
unnamed: LED_USB_DEBUG_RX0.+, R1.2
unnamed: LED_USB_DEBUG_TX0.+, R2.2
unnamed: C4.1, C5.1, C6.1, IC1.4, IC1.17, IC2.8
unnamed: IC1.22, LED_USB_DEBUG_RX0.-
unnamed: IC1.23, LED_USB_DEBUG_TX0.-
USART_RX: IC1.1, IC2.7
USART_RX_ISOLATED: CON_BACKPLANE0.10, IC2.2
USART_TX: IC1.5, IC2.6
USART_TX_ISOLATED: CON_BACKPLANE0.9, IC2.3
USART_VDD: C7.2, CON_BACKPLANE0.8, IC2.1
USB-B_DATA_DM: CON_BACKPLANE0.1, CON_USB-B_DATA0.2
USB-B_DATA_DP: CON_BACKPLANE0.2, CON_USB-B_DATA0.3
USB-B_DEBUG_DM: CON_USB-B_DEBUG0.2, IC1.16
USB-B_DEBUG_DP: CON_USB-B_DEBUG0.3, IC1.15
VBUS_USB-B_DATA_FUSED: CON_BACKPLANE0.3, F2.2
VBUS_USB-B_DEBUG_FUSED: C1.1, C2.2, C3.2, F1.2, IC1.20, R1.1, R2.1
VBUS_USB-B_NF: CON_USB-B_DATA0.1, F2.1

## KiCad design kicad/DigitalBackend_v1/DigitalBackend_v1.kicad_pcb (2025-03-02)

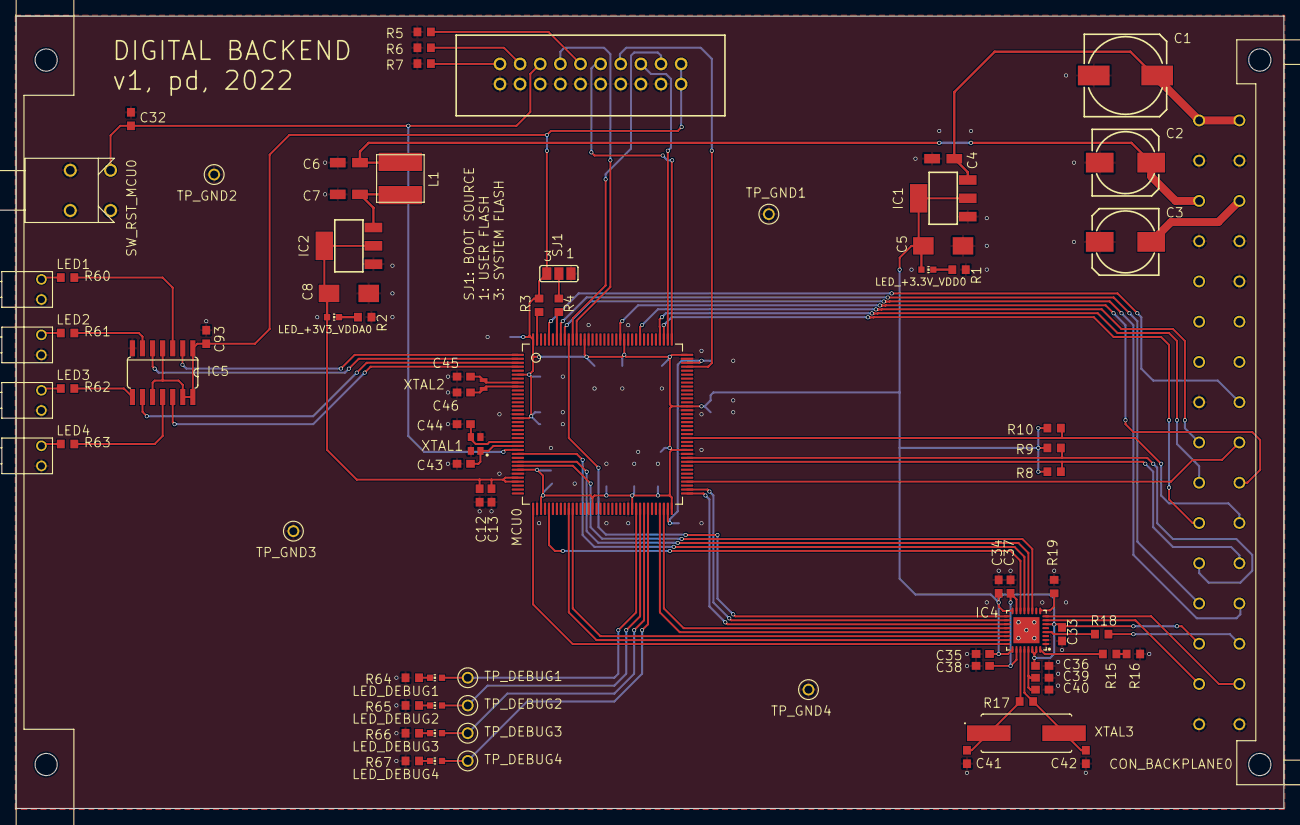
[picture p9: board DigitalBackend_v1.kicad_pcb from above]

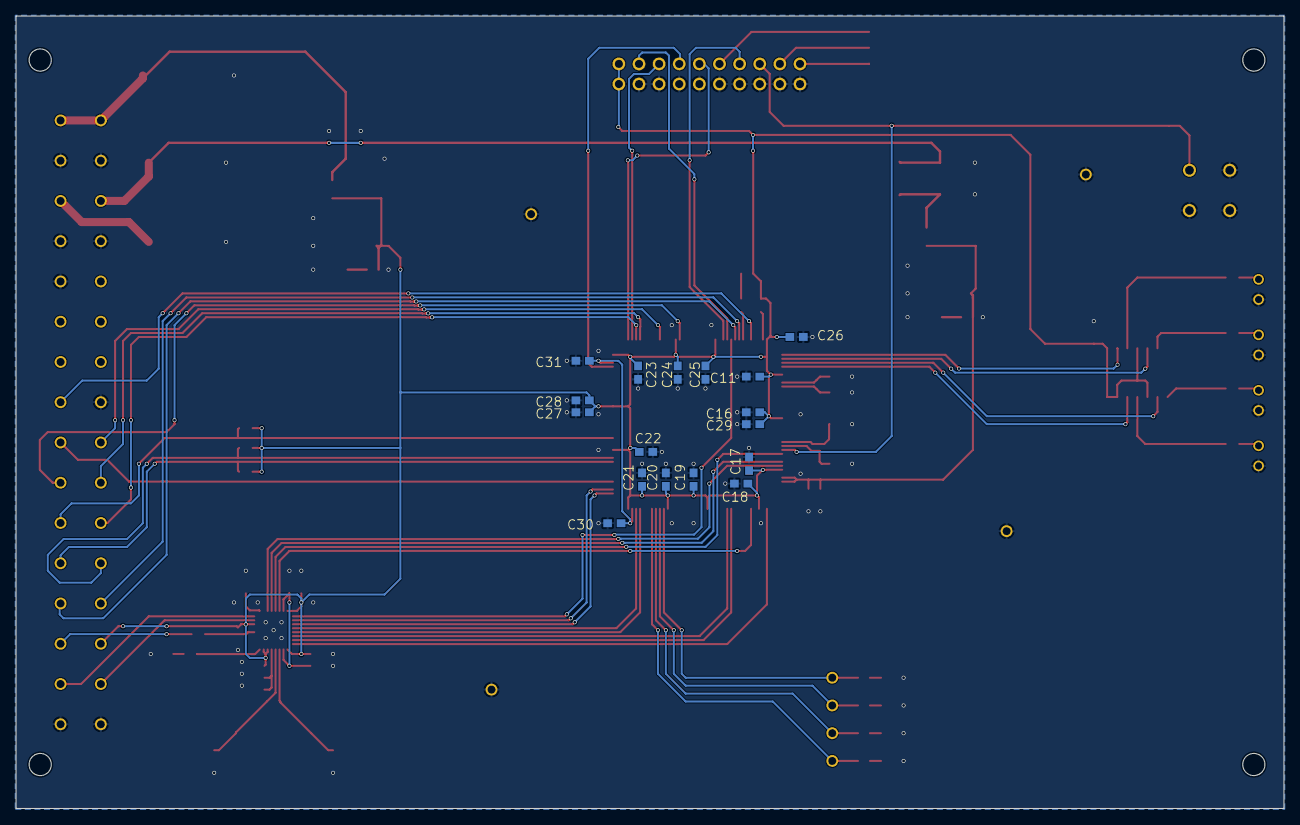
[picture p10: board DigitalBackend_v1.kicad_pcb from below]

Board: 2 copper layers, 160.0 x 100.0 mm, 98 parts (17 on the bottom side), 80 nets.

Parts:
C1: 1000u/16V; 153CLV-1010_18640681
C2, C3: 100u/25V; 153CLV-0810_18640681
C4, C6, C7: 10u; CT3216_23469469
C5, C8: 22u; CT6032_23469469
C11, C12, C27: 1u; C0603_23469469
C13, C16, C17, C18, C19, C20, C21, C22, C23, C24, C25, C26, C28, C32, C33, C34, C35, C36, C37, C40, C93: 100n; C0603_23469469
C29, C38, C39: 4.7u; C0603_23469469
C30, C31: 2.2u; C0603_23469469
C41, C42: 27p; C0603_23469469
C43, C44: 5.6p; C0603_23469469
C45, C46: 15p; C0603_23469469
CON_BACKPLANE0: 09031326921; 09031326921_33573412
CON_JTAG0: TST-110-01-T-DJ; TST-110-01-T-D_23500836
IC1: LM1117IMP-3.3; SOT223_23469477
IC2: LM1117IMP-3.3; SOT223_18698564
IC4: USB3300-EZK; USB3300-EZK_23525048
IC5: 74LVC126AD,112; SO14_85
L1: 100u; VLS6045AF-101M_31421361
LED1, LED2, LED3, LED4: 113-314-04; 113-314-04_33630242
LED_+3.3V_VDD0, LED_+3V3_VDDA0: CHIP-LED0603_259
LED_DEBUG1, LED_DEBUG2, LED_DEBUG3, LED_DEBUG4: CHIP-LED0603_259
MCU0: STM32H753ZIT6; LQFP144_23457850
PCB_BRACKET0: 60807-011; 60807-011_33573280
R1, R2, R64, R65, R66, R67: 750; R0603_23469469
R3, R4, R5, R6, R7, R16: 10k; R0603_23469469
R8, R9, R10: 1.5k; R0603_23469469
R15: 2k; R0603_23469469
R17: 1M; R0603_23469469
R18: 820; R0603_23469469
R19: 4.7k; R0603_23469469
R60, R61, R62, R63: 68; R0603_23469469
SJ1: SJ_2_23508320
SW_RST_MCU0: TP33W008000; TP33W008000_34733409
TP_DEBUG1, TP_DEBUG2, TP_DEBUG3, TP_DEBUG4: RSPRO-1MM-TERMINAL-POST-2622034; RSPRO-1MM-TERMINAL-POST-2622034_23908750
TP_GND1, TP_GND2, TP_GND3, TP_GND4: RSPRO-1MM-TERMINAL-POST-2622034_23908750
XTAL1: XRCGB25M000F2P00R0; XRCGB25M000F2P00R0_23510691
XTAL2: ABS05-32.768KHZ-T; ABS05-32.768KHZ-T_23609575
XTAL3: FOXSDLF-240F-20; FOXSDLF-240F-20_23537815

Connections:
+3V3_VDD: C5.+, C11.1, C16.1, C17.1, C18.1, C19.1, C20.1, C21.1, C22.1, C23.1, C24.1, C25.1, C26.1, C27.1, C28.1, C29.1, C33.1, C34.1, C35.1, C36.1, C93.2, CON_BACKPLANE0.27, CON_JTAG0.1, CON_JTAG0.2, IC1.2, IC1.TAB, IC4.6, IC4.16, IC4.25, IC4.30, IC4.31, IC5.1, IC5.4, IC5.10, IC5.13, IC5.14, LED_+3.3V_VDD0.A, MCU0.6, MCU0.17, MCU0.30, MCU0.39, MCU0.52, MCU0.62, MCU0.72, MCU0.84, MCU0.95, MCU0.108, MCU0.121, MCU0.131, MCU0.144, R3.2, R8.2, R9.2, R10.2, SJ1.3
+3V3_VDDA: C8.+, C12.1, C13.1, IC2.2, IC2.TAB, LED_+3V3_VDDA0.A, MCU0.32, MCU0.33
+5V: C1.+, C4.+, CON_BACKPLANE0.1, CON_BACKPLANE0.2, IC1.3
+12V: C2.+, C6.+, CON_BACKPLANE0.5, L1.1
-12V: C3.-, CON_BACKPLANE0.6
DEBUG1: LED_DEBUG1.A, MCU0.63, TP_DEBUG1.P$1
DEBUG2: LED_DEBUG2.A, MCU0.64, TP_DEBUG2.P$1
DEBUG3: LED_DEBUG3.A, MCU0.65, TP_DEBUG3.P$1
DEBUG4: LED_DEBUG4.A, MCU0.66, TP_DEBUG4.P$1
GND: C1.-, C2.-, C3.+, C4.-, C5.-, C6.-, C7.-, C8.-, C11.2, C12.2, C13.2, C16.2, C17.2, C18.2, C19.2, C20.2, C21.2, C22.2, C23.2, C24.2, C25.2, C26.2, C27.2, C28.2, C29.2, C30.2, C31.2, C32.1, C33.2, C34.2, C35.2, C36.2, C37.2, C38.2, C39.2, C40.2, C41.2, C42.2, C43.2, C44.2, C45.2, C46.2, C93.1, CON_BACKPLANE0.3, CON_BACKPLANE0.4, CON_BACKPLANE0.7, CON_BACKPLANE0.8, CON_BACKPLANE0.10, CON_BACKPLANE0.15, CON_BACKPLANE0.31, CON_BACKPLANE0.32, CON_JTAG0.4, CON_JTAG0.6, CON_JTAG0.8, CON_JTAG0.10, CON_JTAG0.12, CON_JTAG0.14, CON_JTAG0.16, CON_JTAG0.18, CON_JTAG0.20, IC1.1, IC2.1, IC4.1, IC4.2, IC4.33, IC5.7, LED1.-, LED2.-, LED3.-, LED4.-, MCU0.16, MCU0.31, MCU0.38, MCU0.51, MCU0.61, MCU0.83, MCU0.94, MCU0.107, MCU0.120, MCU0.130, R1.2, R2.2, R5.1, R6.1, R7.1, R16.1, R19.1, R64.2, R65.2, R66.2, R67.2, SJ1.1, SW_RST_MCU0.GND1, SW_RST_MCU0.GND2, SW_RST_MCU0.P1, TP_GND1.P$1, TP_GND2.P$1, TP_GND3.P$1, TP_GND4.P$1, XTAL1.2, XTAL1.4
I2C4_NINT: CON_BACKPLANE0.22, MCU0.87, R10.1
I2C4_SCL: CON_BACKPLANE0.24, MCU0.81, R8.1
I2C4_SDA: CON_BACKPLANE0.23, MCU0.82, R9.1
JTCK/SWCLK: CON_JTAG0.9, MCU0.109
JTDI: CON_JTAG0.5, MCU0.110
JTDO/TRACESWO: CON_JTAG0.13, MCU0.133
JTMS/SWDIO: CON_JTAG0.7, MCU0.105
LED1: IC5.2, MCU0.1
LED2: IC5.5, MCU0.2
LED3: IC5.9, MCU0.3
LED4: IC5.12, MCU0.4
unnamed: C37.1, C38.1, IC4.15, IC4.26
unnamed: MCU0.143, R3.1
unnamed: MCU0.138, R4.2
unnamed: C7.+, IC2.3, L1.2
unnamed: R4.1, SJ1.2
unnamed: CON_JTAG0.19, R7.2
unnamed: CON_JTAG0.17, R6.2
unnamed: CON_JTAG0.11, R5.2
unnamed: C45.1, MCU0.8, XTAL2.1
unnamed: C44.1, MCU0.23, XTAL1.3
unnamed: C43.1, MCU0.24, XTAL1.1
unnamed: C39.1, C40.1, IC4.29
unnamed: LED1.+, R60.2
unnamed: LED2.+, R61.2
unnamed: LED3.+, R62.2
unnamed: LED4.+, R63.2
unnamed: R15.1, R16.2
unnamed: IC4.32, R15.2
unnamed: C41.1, IC4.27, R17.2, XTAL3.1
unnamed: C42.1, IC4.28, R17.1, XTAL3.2
unnamed: IC4.4, R18.1
unnamed: IC4.9, R19.2
unnamed: C46.1, MCU0.9, XTAL2.2
unnamed: LED_+3.3V_VDD0.C, R1.1
unnamed: LED_+3V3_VDDA0.C, R2.1
unnamed: IC5.3, R60.1
unnamed: IC5.6, R61.1
unnamed: IC5.8, R62.1
unnamed: IC5.11, R63.1
unnamed: LED_DEBUG1.C, R64.1
unnamed: LED_DEBUG2.C, R65.1
unnamed: LED_DEBUG3.C, R66.1
unnamed: LED_DEBUG4.C, R67.1
NJTRST: CON_JTAG0.3, MCU0.134
NRST: C32.2, CON_JTAG0.15, MCU0.25, SW_RST_MCU0.P3
SPI2_MOSI: CON_BACKPLANE0.18, MCU0.76
SPI2_NSS: CON_BACKPLANE0.16, MCU0.140
SPI2_SCK: CON_BACKPLANE0.17, MCU0.117
SPI3_MISO: CON_BACKPLANE0.19, MCU0.112
SPI3_MOSI: CON_BACKPLANE0.20, MCU0.122
SPI3_SCK: CON_BACKPLANE0.21, MCU0.111
ULPI_CLK: IC4.14, MCU0.41
ULPI_DATA0: IC4.24, MCU0.37
ULPI_DATA1: IC4.23, MCU0.46
ULPI_DATA2: IC4.22, MCU0.47
ULPI_DATA3: IC4.21, MCU0.69
ULPI_DATA4: IC4.20, MCU0.70
ULPI_DATA5: IC4.19, MCU0.73
ULPI_DATA6: IC4.18, MCU0.74
ULPI_DATA7: IC4.17, MCU0.135
ULPI_DIR: IC4.12, MCU0.28
ULPI_NXT: IC4.11, MCU0.29
ULPI_STP: IC4.13, MCU0.26
USART1_RX: CON_BACKPLANE0.25, MCU0.137
USART1_TX: CON_BACKPLANE0.26, MCU0.136
USB_DATA_DM: CON_BACKPLANE0.30, IC4.8
USB_DATA_DP: CON_BACKPLANE0.29, IC4.7
VBUS_USB_DATA: CON_BACKPLANE0.28, R18.2
VCAP: C30.1, C31.1, MCU0.71, MCU0.106

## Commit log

2025-02-28 Update README.md
    add link to case parts
2025-03-02 init to convert PCB files to KICAD
    [AnalogConversion_v3.kicad_pcb, Backplane_v1.kicad_pcb, DigitalBackend_v1.kicad_pcb, PowerSupply_12V_v1.kicad_pcb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]
